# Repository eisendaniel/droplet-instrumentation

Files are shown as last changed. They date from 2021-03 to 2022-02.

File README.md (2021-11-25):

# Repository Directory Structure

### Documents

Any files which aren't _Literature_, i.e. anything that won't or can't be cited.

### Literature

A flat folder containing PDF copies of anything that will or could be cited in the reports: journal articles, tech notes, etc.  There should be a BibTeX `.bib` bibliography file at the same level as the PDF files, for use with the [JabRef](http://www.jabref.org) open source bibliography and reference manager.

### Presentations

The files used in any presentations, including the final presentation.

VBUS
* R, Matlab, etc. files, containing _only_ the figures used in the report at this level.
* One sub-folder "Figures" to keep figures organised.

Home: O
Res: 55
Targ: 172

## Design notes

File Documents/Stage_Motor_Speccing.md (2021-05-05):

# XYZ Stage Motorisation

Applying motorisation and actuation to the droplet dispensing process and support stage. Pulse Z to detach droplet, rotate around Z to position pipette etc.

## Suppliers

servocity.com -   they have a variety of servos and motors, as well as 
mechanical mounting options. note these are largely imperial 
measurements. (mil, inchs, feet etc)

gobilda.com - other side of servocity, dealing with metric units.

pololu.com - large selection of steppers motors and servos.

robotshop.com - another large selection of servos and steppers.

* All of these suppliers are based in North America, 
* 7-10 days from there (Loss of guarantee due to COVID).

## Driving Options

###  Hall Encoder Brushed N20 motors

e.g https://www.servocity.com/90-rpm-micro-gear-motor-w-encoder/
* $USD 12-20
* 90-4900RPM
* Drive a worm gear to rotate platform
* Require manual position control

### Worm Gear set
* https://www.servocity.com/27-1-worm-gear-set-1-4-bore-worm-hub-mount-worm-gear/

### Servo driving
e.g. https://www.servocity.com/hs-311-servo/
* When driving with a uC, wide signal ~200 degrees
* Pulse to position
* Nylon - wear/no backlash
* Metal - vis versa

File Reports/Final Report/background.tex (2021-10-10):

\chapter{Background and Related Work}\label{C:back}

\section{Droplet Impact \& Evaporation}
Droplet Impact and Evaporation experiments have a consistent list of instrumentation requirements and variable considerations. At its core is the substrate upon which the droplet is deposited, this can be held at a variety of temperatures, have differencing surface and material properties that all affect the temperature evolution and physical interaction between the droplet and its surface. Secondly is the method of droplet dispensing or deposition, and third is the method through the which the experiment controls for, account for, or just records the variety of affecting factors.      

\subsection{Other Approaches}
In literature, there exists a variety of rigs for similar experiments. These were explored to gauge a range of what factors were controlled (and measured) and with what approaches. In summary:
\begin{itemize}
    \item Controlled environmental factors with basic box \cite{step_book} or measured factors only \cite{measure_only}.
    \item Controlled for droplet position and volume with hard-mounted pump plus needle, but lacks environmental control or automation, and there is no top-view camera \cite{non_newt} \cite{fixed_pump}.
    \item Incorporated stepper motor driven automation, but no environmental control or monitoring \cite{motors}.
    \item Full environmental chamber and fixed droplet pump, but the single camera, has the separate uncontrolled rig for top view \cite{duel_rig}.
\end{itemize}

\section{Background on Stepper motor control}
This section will cover the background of controlling bipolar stepper motors via a step/direction style driver setup, as its concepts will be mentioned later in the report. This is a focused background on the key considerations and requirements when designing for and operating this specific subset, and by no means applicable to all driving and specific motor choices.

The stepper motors provide precise positioning and are capable of moving their rotor to a specified position and holding that position at a wide range of load torques. This capability makes the stepper motors popular in optics, medical instruments, factory automation, and industrial equipment.

The typical topology of a stepper driving system (based around the step/direction method) consists of a controller, driver, and stepper motor. The controller provides a direction  signal and step pulses, while the driver converts these signals into actual electrical power and supplies them to the motor. The stepper motor moves in steps, each step covering one step angle, which can be described as the rotor displacement corresponding to one step pulse \cite{step_app}.

Stepper motors typically have a step size specification (e.g. 1.8° or 200 steps per revolution), which applies to full steps. Step/direction drivers usually provide a 'microstepping' mode which increases the resolution by allowing intermediate step locations, which are achieved by energising the coils with intermediate current levels \cite{step_book}.

The last major consideration in driving steppers is controlling the start-up and stopping speeds for the controller's provided pulse train to the driver. As the motor is a mechanical device in the real world, expecting a perfect impulse response will lead to driving failure. Inertia ratio is critical to stepper motor acceleration \cite{step_book}. Too great a difference in inertia ratio between system and motor risks missed steps or stalling the coils. So when starting a stepper motor, acceleration and deceleration should happen through pulses to the motor that starts slowly and gradually quicken in a process called ramping.

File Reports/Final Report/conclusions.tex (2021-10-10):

\chapter{Conclusions and Future Work}\label{C:conclusion}

\section{Conclusions}

The aims of this project were to control for variations in droplet morphology; droplet position and volume, providing an improvement over the previous system. Produce an extendable platform that enabled the experimental process to be automated/centrally controlled to speed up the procedure. Provide a data collection system for uncontrolled factors. 
These goals were chosen with the hypothesis that improving the system's performance in these aspects would carry through to an improvement in the inconsistent results observed in the previous iteration of the system.  

To control for droplet volume and provide a method for variable volume, this project utilised a pre-calibrated electronic pipette as the central droplet dispensing tool that is interfaced with to provide remote GPIO control. Automation, user control and positional control was achieved via a serial command-driven stepper motor controller that drove the motion of a micrometer controlled XYZ stage mounted upon an optical breadboard.   

\subsection*{Successes}
The use of a pre-calibrated electronic pipette eliminates volume variation to a point beyond the scope of this projects ability to measure, but more importantly, the mechanical system was confirmed to be stable enough to support the full variable volume range from 0.5 to 10 microlitres.

The stepper motor driving system parameters were successfully tuned to reduced pipette tip settling oscillation below 1mm in 1s and achieves consistent and exact positioning. This precision in instrumentation control resulted in the reduction in droplet positional offset  variance from 0.296mm to 0.018mm.

From initial analysis of the collected temperature profiles, this project can preliminarily confirm the hypothesis that improved positional and volume consistency will result in greater consistency in experimental results. Though more data is needed.

The firmware and controller implemented fully supports input of predefined command sequences that allows a user to quickly run the same complex experimental procedure much time, with the exact same instrumentation performance.   

\subsection*{Drawbacks}
Major drawbacks of the resulting design include the XY positional locking of the pipette stage due to static Z motor mounting on the breadboard. This results in any required adjustment to the camera, substrate and reservoir to be carried out to fit the pipette stage position.

This implementation lacks auto-homing to set zero position, and additionally due to the permanent magnetic pole of the stepper motor stator combined with the drivers micro steppers, the user can request an invalid holding position as home. This cannot be maintained due to current limits and will snap away from it. This should however be evident in the setup stage of the experiment.  

\section{Future Work}
As stated this project produced an extendable platform from which a variety of features can be implemented.
\begin{itemize}
    \item User-Friendly Graphical Control to interface with serial command controller. As of now, there exists a LabVIEW script that can interface with the serial input of the controller but more in-depth user-friendly version would be a great step up in the usability of the system.
    \item Due to the projects nature combined with an inopportune COVID19 lockdown the integration of homing switches to automate setup was planned but not implemented. This addition would increase setup speed and usability.
    \item Utilise included GPIO breakout header to synchronise external data acquisition
    \item Further investigate Temperature evolution with varied volume, substrates, cleaning techniques
    \item Add enclosure to isolate air currents and further control variables.
\end{itemize}

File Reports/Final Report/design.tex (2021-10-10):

\chapter{Design}\label{C:des}

\section{Project Specifications and Justifications}
Given the results of the initial evaluation, the project can now be constrained. Its main goals are to eliminate volume variation, control for droplet position, enable automation to reduced time between consecutive runs. It will not control, but provide data-logging for the environmental effectors; temperature, humidity, pressure.

From this there is a number of requirements to consider:

\begin{itemize}
    \item \textbf{Mechanical Stability}
    \item \textbf{Droplet Position Repeatability}
    \item \textbf{Consistent and Variable Volume}
    \item \textbf{Process Automation}
    \item \textbf{System Expandability}
\end{itemize}

The project will be evaluated on how it meets the above Specifications, its ability to control for volume and positional accuracy and repeatability as well as how it adds/improves automation, provides environmental data and allows an extension.

\section{Drop Dispensing and Volume Control}

At the core of the system is the liquid droplet dispensing hardware. The two core limitations of the initial setups manual syringe were fixed volume dispensing and the observed inconsistency in drop volume. In order to address these, an alternative solution is required to provide a core that allows the rest of the project to control and automate positioning, dispensing and liquid refilling. It was decided early on that the bulk of custom design would be focused on the motorisation hardware, custom mounting, and the driving software so the dispenser would be handled by a pre-existing product. The product selected for this is a single channel electronic pipette from Labnet, P3600L-10. 

\begin{figure}[h]
    \centering
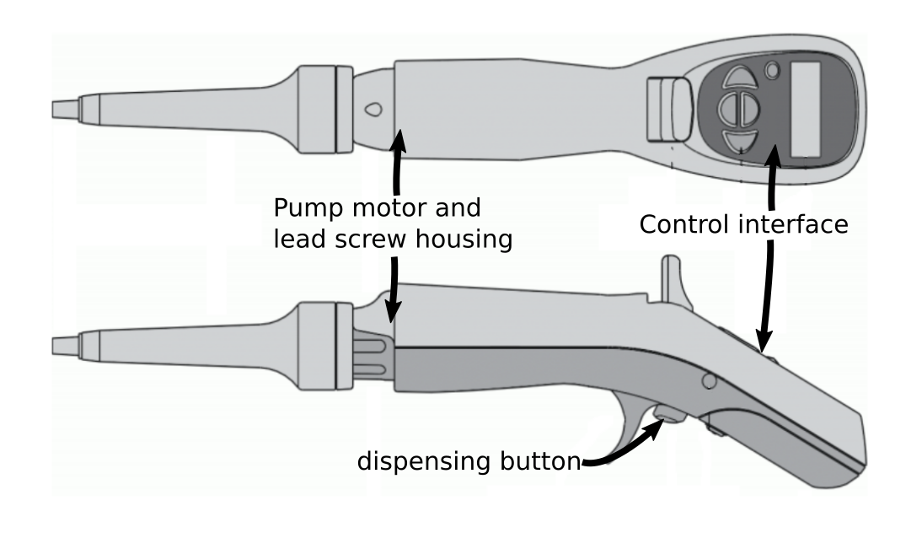
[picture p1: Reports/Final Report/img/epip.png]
    
    \caption{Labnet Excel P3600L-10}
    \label{fig:pip_dia}
\end{figure}

This product comes recalibrated and verified to dispense a droplet at a specified volume with an accuracy of $\pm 4.0\rightarrow \pm 1.0 \%/\mu L$ over the selection range of $0.5\mu L \; to \; 10\mu L$. This range represents the full range the pipette itself is capable of drawing and dispensing, configured via the front panel [see \ref{fig:pip_dia}], but an evaluation of the integrated system is required to confirm the mechanical stability is high enough to prevent a high volume drop from prematurely detaching, as well as if its capable of depositing the minimum volume on the substrate.

Liquid refilling and dispensing are handled via the button on the back [\ref{fig:pip_dia}] and to enable the instrumentation to centrally control this, the planned approach was to break out the underlying switch contacts as GPIO inputs. The full process and results will be fully explored in this reports implementation system.

\section{Mechanical Design}

The goals for the mechanical aspects of this project are to provide a mounting interface to allow for the movement and positioning of the electronic pipette, mount to the optical XYZ stages, and transfer the driving force from the stepper motors to the instrumentations mechanisms.

All mechanisms share the requirements to fit compactly and correctly on the optical breadboard baseplate. Be designed in such a way as to minimise backlash and prevent vibrations from propagating and resonating through the system. As this could interfere with droplet dispensing; increasing pipette tip overshoot and settling times, causes prematurely drop detachment and generally decreasing the key performance metrics.

\subsection{Rotating Pipette Mount}

The first half of the main assembly is Pipette Stage. In order to manoeuvre the pipette from the reservoir to substrate stack, the pipette needs to be held at a specific height and angle to roughly match the central stage (as it is Z adjustable) and rotate between these two points.

To achieve the mounting stage consists of three main parts: 
\begin{itemize}
    \item Pipette clamping and Angled mount: Responsible for securely fastening the e-pipette at the correct angle.
    \item Laser Cut Mounting Tower: Sets pipette height and connects pipette to the motor.
    \item Motor shaft interface and Stage Fastening: Rotation is directly driven via the motor, thus the assembly is mounted to the motor shaft. 
\end{itemize}

Dimensional Specifications: Pipette height of 130mm (from breadboard) and angle of 36.25 degrees.
These specifications are used to derive the full dimensions of the following assemblies.

The electronic pipette form-factor is ergonomic-hand to fit in human hand-so the clamping mechanism to fit it to the tower plate itself was challenging to design to successfully restrict its rotation and backlash. 3D printed PLA c-clamps were the perused approach to capitalise on the materials ability to deform and to aid in rapid implementation and testing.

\begin{figure}[h]
    \centering
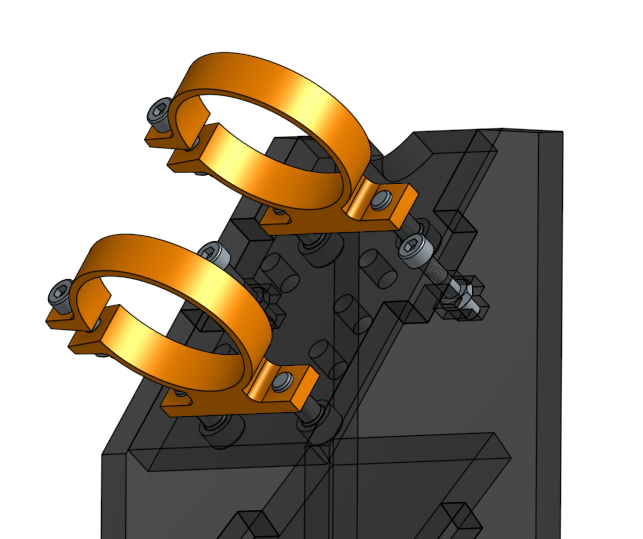
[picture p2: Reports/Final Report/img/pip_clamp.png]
    
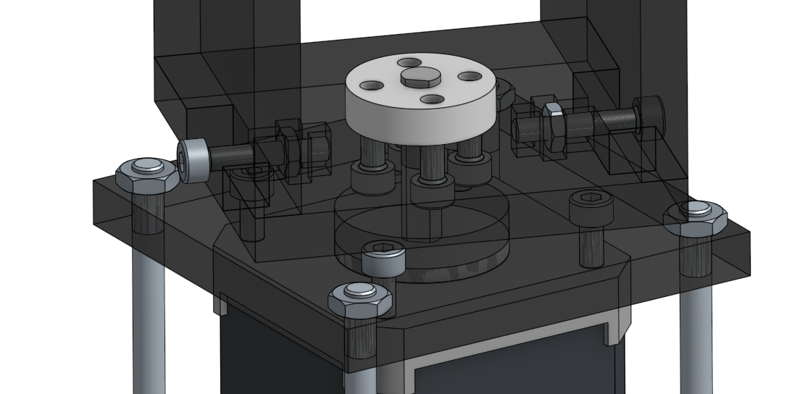
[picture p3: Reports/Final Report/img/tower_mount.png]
    
    \caption{Left: Pipette Clamps and Tower, Right: Towers base mounting to the motor shaft}
    \label{fig:tower}
\end{figure}

The base design used to accomplish this was a 3D-printed ring clamp [Left:\ref{fig:tower}] meant to be tightened and fit to the unique form of the pipette body. A variety of ring sizes and gap distances were printed and test fitted. From this, it was determined that a ring diameter of 32mm and a gap of 6mm fits and deforms to the shape of the pipette. However, there was still some rotation and slip so a notch was cut into the acrylic angle plate [Left:\ref{fig:tower}] to slot the pipettes support rest and a second ring clamp (36mm) attached lower down of the body.

To connect the tower assembly to the motor and optical stage\dots

\subsection{Z micrometer Control}

In order to control the height of the pipette tip; to enable automated refilling and to place the dispensed droplet onto the substrate the Z height of the optical stage needs to be motorised. The Z height has a manual control in the form of an adjustment micrometer that allows for 10mm of travel, but this presents the first problem in design.
The micrometer travels linearly throughout the adjustment, i.e. if the stage raises 10mm the knob will retract 10mm also. Due to this a custom shaft coupler is required to interface a fixed motor to the moving knob.

\begin{figure}[h]
    \centering
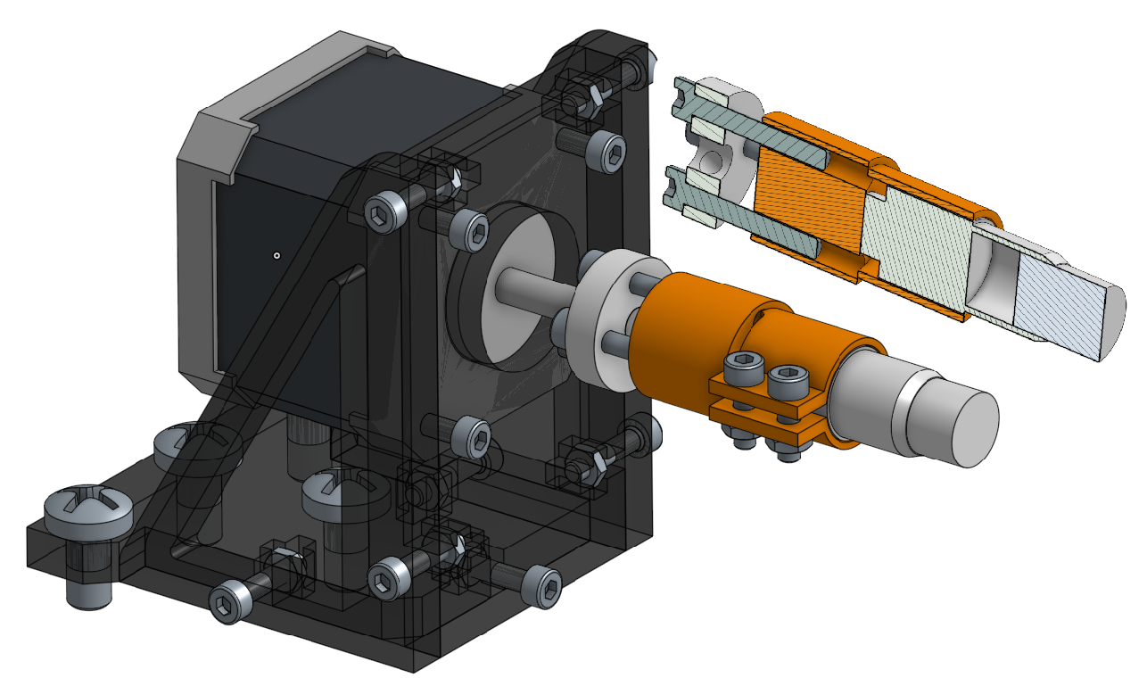
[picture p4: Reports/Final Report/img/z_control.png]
    
    \caption{Z Driving Motor and Sliding Shaft Coupler}
    \label{fig:z_coup}
\end{figure}

The figure above[\ref{fig:z_coup}] shows the assembled design. One end of the coupler is an extended c-clamp that mates with the knurls knobs of the micrometer and the other is a solid piece with 4 M3 clearance holes. These holes interface with a universal shaft-hub mount with 4 M3 machine screws that transfer the rotation of the motor and allow the coupler and knob to slide away over the course of a movement.

The key limitation of this design is that is constrains the XY position of the stage to a single setting. This is due to the motor being fastened to the breadboard baseplate more stability, alignment and vibration reduction. Because of this it moves the fine positioning to the other stages in the setup; substrate stack and cameras. 

\section{Electronic Design}

\subsection{Motors}
The motion required for the motors in this system is to provide rotation about the vertical axis to the mounted pipette, to swing from above the substrate to out of the camera view and over a refill reservoir, as well as continuous rotation to interface the Z axis control for droplet depositing and possible refilling.

Stepper motors allow for both precise position control without the need for a feedback system and are capable of continuous rotation. In comparison, brushed/brushless DC motors require encoders for positional control and servos may do either but not both continuous rotation and positioning.

NEMA17 standard-sized steppers were chosen to best fit the dimensions of the XYZ optical stage (60mm plate to 40mm motor frame) with room for fastening hardware. That left two choices for the top R stage motor; full size 38mm high frame or shorter pancake frame. Even though the pancake frame would reduce the overall height of the system, the shaft length available for this motor is less only 7mm and would greatly restrict the mounting options of the tower to the motor. For this reason, 2 NEMA17x38mm Stepper motors were chosen.

\subsection{Motor Driving}

\subsubsection*{The Requirements}
To drive the selected stepper motors, discrete step/direction style micro stepping drivers were chosen. This allows for the design to be flexible with its electronics placed to accommodate the experimental needs. Allows for a fairly agnostic choice for the controller to supply the control signals, and standardised pinouts allow for requirement flexibility and replacements.

\begin{table}[h]
    \centering
    \begin{tabular}{|l|l|l|l|l|}
        \hline
        \textbf{}     & \textbf{A4988} & \textbf{DRV8825} & \textbf{STPIN820} & \textbf{DRV8834} \\ \hline
        Step Res      & 1/16           & 1/32             & 1/256             & 1/32             \\ \hline
        Logic Level   & 3V3/5V         & 3V3/5V           & 3V3/5V            & 3V3/5V           \\ \hline
        Current Limit & 1A             & 1.5A             & 0.9A              & 1.5A             \\ \hline
        Drive Voltage & 8-35V          & 8.2-45V          & 7-48V             & 2.5-10.8         \\ \hline
    \end{tabular}
    \caption{Comparison of considered drivers}
\end{table}

Main consideration for device choice are: micro step resolution, driving current limit (passively cooled), and configuration pinout.

\subsubsection*{The Choice}
The DRV8825 was ultimately chosen.
\begin{itemize}
    \item High microstepping resolution, lower than the STPIN820 but cheap high-resolution driver is prone to step skipping \cite{step_book}
    \item Highest driving current as torque requirements are unknown for this design the headroom is nice even if it isn't used, especially as it will run cooler at lower power draw.
    \item It ranked above the DRV8834 due to it configuration pins (to set microstepping mode) as it provides all 3 pins without the requirement to leave pins floating as a setting thus allowing for full software control.
\end{itemize}

\newpage
\subsection{Environmental Monitoring}

Although the aim of this project is to only control the position and volume of the droplet in the experiment, to at least fully address the list of affecters [covered in \ref{C:init_eval}] the environmental factors recorded are: \textbf{Temperature, Barometric Pressure, Relative Humidity}.

As this section of the project doesn't note share resources with the main motorised assembly it key design considerations was simplicity and function.
Therefore, the environmental monitor is not required to have any integration with the main controller or data logging capabilities.

To meets these requirements the monitor was decided to be a low power microcontroller + OLED display stack that polled environmental sensor peripherals. This would be battery powered and utilised low power sleep modes to extend lifetimes.

To facilitate ease of implementation the microcontroller + display combo was chosen to be an Adafruit feather and OLED stack. specifically the RP2040 for its low power capabilities and JST LiPO battery connector.

Sensor options considered were the discrete LPS22/25 for pressure and DHT11/22 for humidity and temperature or the fully integrated BME280 for all measurements. 

\section{System Overview}

\begin{figure}[h]
    \centering
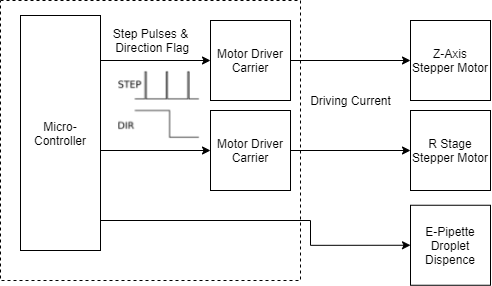
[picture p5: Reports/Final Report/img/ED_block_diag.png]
    
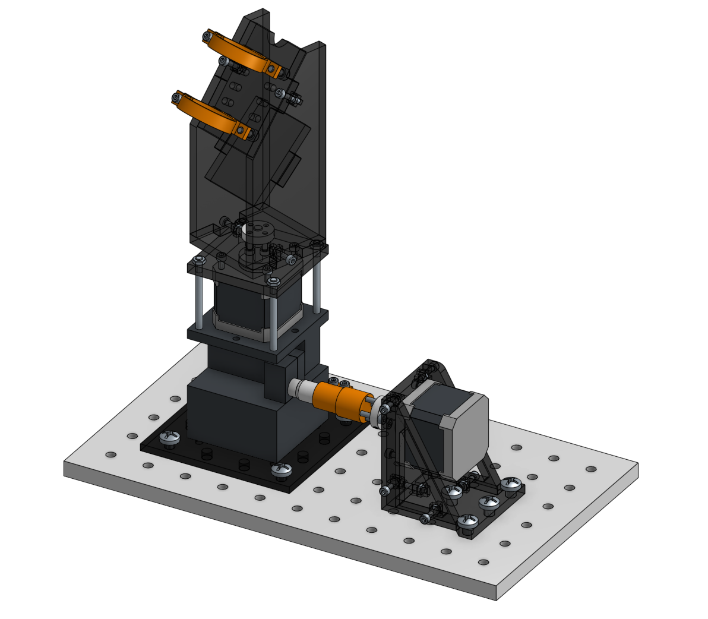
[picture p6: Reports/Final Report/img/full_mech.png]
    
    \caption{Left: Instrumentation Architecture, Right: Full CAD Design and Layout on optical breadboard}
    \label{fig:sys_des}
\end{figure}

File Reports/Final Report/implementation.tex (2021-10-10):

\chapter{Implementation}\label{C:imp}
The implementation process took the planned designs and selected hardware and constructing an integrated system. This provided an opportunity to test, iterate finalise the designs and approaches of the project.      

\section{Mechanical Components}
Implementing the mechanical components of the system covered the material choice, manufacture and adjustment of the motor mounting brackets, shaft couplers and interfacing and pipette mounting and supports. Considerations taken were speed of iterations. Flexibility in adapting specific dimensions to suit needs and to maximise reliability and stability. 

\subsection{Rotating Pipette Mount}
The C-clamp's design did not fundamentally change from the initial design, and remained the duel clamping system with matched internal circumferences. They did however go through many smaller interactions to achieve the preferred performance. Firstly, obtaining the required internal circumference of the clamps from the asymmetric body of the pipette was taken using a length of string was used to at the points of intended fastening. The clamping pressure then deformed the initially circular parts to the ergonomic form of the pipette body.

\begin{wrapfigure}{r}{0.3\textwidth}
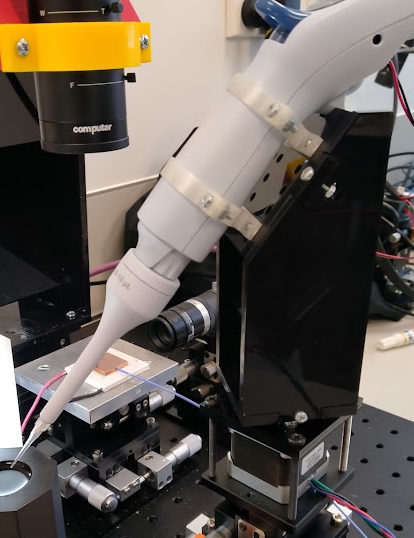
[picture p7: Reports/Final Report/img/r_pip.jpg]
    
    \caption{Final constructed Pipette stage mounting tower w/ clamps and motor}
\end{wrapfigure}

This process, and the resulting measurements of 32mm and 36mm remained unchanged.
However, the ring thickness was varied and tested. 3 options were 3D printed and trialled; 1mm, 1.5mm, and 2mm. This thickness affected the clamps ability to deform to the shape of the pipette, how rigid the mounting was and the strength at the clamping screw holes.

1mm was used for the longest initially, but had a noticeable woggle as well and resulting in the screw hole delaminating from the ring due to flexing in the plastic. After this failure, the 1.5 and 2mm versions were printed and trialled for a shorter period. The 2mm provided much better strength, showing no noticeable degradation at points of high-stress concentration. However where this thickness failed was in deforming, the added rigidity was just too inflexible to ever fully clamp and resulted in play/slippage. Given this, two 1.5mm version were printed to compromise and successfully deformed and remained intact over the remaining project time.   

Another area of tweaking was the screw tolerance. These pieces were designed to take advantage of the plastics deformation to also allow for the screws to cut their own threads as provide a stronger grip. As the screw is initially inserted a too smaller hole can result in splitting delamination of the plastic layers, via experimentation, a +0.2mm diameter tolerance allowed for retaining that 'self-tapping' characteristic while maintaining structural integrity. 

The tower itself was designed to be fully laser cut from acrylic to minimise [material] flexibility and to aid to modularity. This allowed the height to be adjustable by cutting different side pieces for example. This did not deviate from design, but initially, the tower was glued together to reduce weight but this was quickly scrapped for machine screw bolting, with the intention that any oscillations or resonance in the system would be tuned for on the motor driving side of the project.

\subsection{Z micrometer Control}

The Z height adjustment represents the most sensitive mechanical system and required careful measurements to axially align the micrometer knob and the shaft as well as matching the coupler length to accommodate the discrete fastening points of the optical breadboard. 

\begin{wrapfigure}{r}{0.42\textwidth}
    \centering
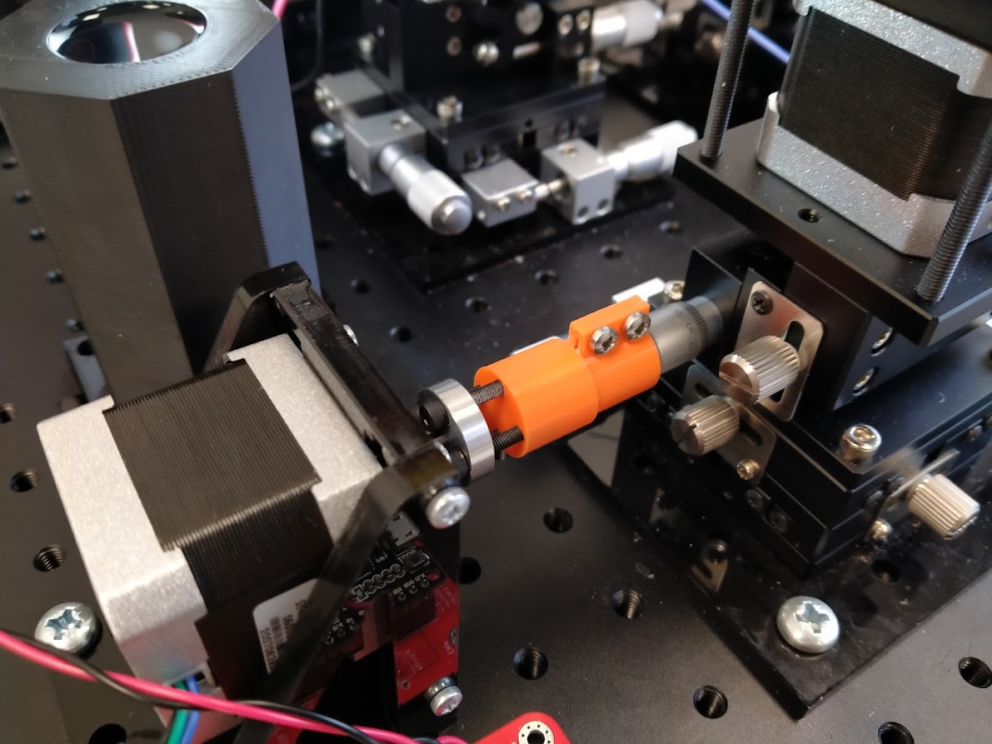
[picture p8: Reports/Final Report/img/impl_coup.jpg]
    
    \caption{Constructed Motor mount and sliding coupler interfacing with the z-micrometer of the XYZ stage}
    \label{fig:z_coup}
\end{wrapfigure}

The figure above \ref{fig:z_coup}shows the Z-motor statically mounted to the breadboard with a laser-cut bracket assembly. This, along with the aforementioned tight tolerance requires presented the first problem to overcome with mechanical performance.

The initial z-coupler was printed with a 1mm defect in it radius as too small M3 screw holes. This cause splitting under high load as well as large vibrations that propagated through the whole system as was causing premature droplet detachment.

After reprinting the coupler, these vibrations were greatly reduced by still present. To combat this, the motor driving parameters were adjusted, slowing the signal speed from 10 revolutions per second until it no longer resonated during the adjustment. Final parameters were 6 rev/s and 100 rev/s/s.

\section{Electronic Components}

The aim of the electronics in this project is to provide an interface for the host computer to send commands with the controlling microcontroller and supply and support the stepper driving stages and their required current. The microcontroller receives command strings over serial USB and parsed them and executes them either at PWM control signals to the STEP inputs of the drivers or digital flag signals to the pipette. The driver requires a motor supply voltage of 8.2 – 45 V. This supply should have appropriate decoupling capacitors close to the board, and it should be capable of delivering the expected stepper motor current.

These decoupling capacitors are to act as reservoirs for high loads and shield the onboard low-ESR ceramics from LC voltage spikes. These spikes can exceed the 45 V maximum voltage rating for the DRV8825 and permanently damage the board, even when the motor supply voltage is as low as 12 V. This was addressed with the addition of  a pair of 100u electrolytic capacitors across the motor power rails right next to the carriers.

\begin{figure}[h]
    \centering
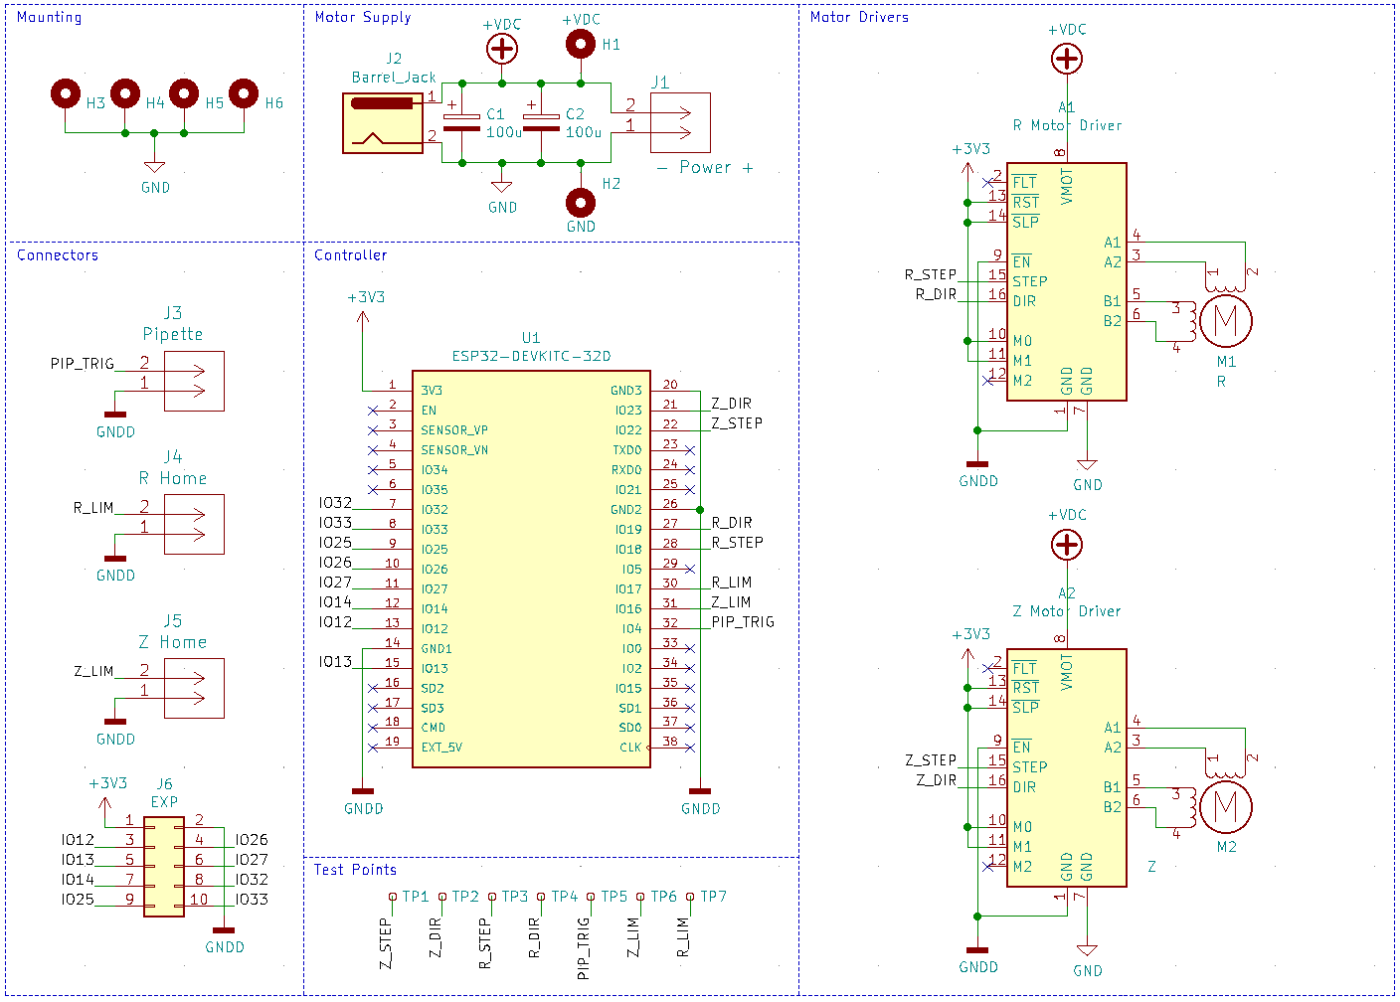
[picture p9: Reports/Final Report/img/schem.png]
    
    
    \caption{Left: Controller Schematic and Right: Constructed PCB}
    \label{fig:schem_pcb}
\end{figure}

The figure\ref{fig:schem_pcb} shows the final electrical implementation and state the controller PCB (only partially populated due to COVID shipping delays). Note that this design included unfulfilled homing switch pads, as well as a 10 pin GPIO breakout for future expansion; i.e. external data acquisition syncing or other communication options.

The final consideration for this construction is whether the driver carriers require heatsinking or cooling. The DRV8825 driver IC has a maximum current rating of 2.5 A per coil, but the current sense resistors further limit the maximum current to 2.2 A, and the actual current you can deliver depends on how well you can keep the IC cool. The carrier’s printed circuit board is designed to draw heat out of the IC, but to supply more than approximately 1.5 A per coil, a heat sink or other cooling method is required. To obtain the systems requirements, both motors were supplied with a 15V DC motor voltage and the total current draw was tested at holding and under load.

This resulted in a max single driver holding current of 0.41A and a peak load current of 0.58A. 
This is well below the uncooled limit so no cooling solution was supplied.

\subsection{Motor Driving}
\subsection{Setup and Requirements}
To meet the driving requirements of the stepper motors outlined in this reports background [\ref{C:back}], preventing stalling and minimising harsh start stop behaviour that could cause unwanted vibrations, the controller and driver must be verified to be able to supply the step pulse train with ramping speeds and characterise the motors to ensure no steps are skipped. If this occurs the open loops control scheme will mean that the systems positional accuracy will fail.  

Test driving firmware was implemented on an ESP32 to validate its ability in producing the required pulse train step signal. The controller was required to produce N steps (pulses) at a set average speed, and ramp-up and down that pulse speed at the head and tail of that signal.

Set values of 200 steps forward and back, at a speed of 200 steps per second, with max acceleration of 800 steps per second per second:

These pulses were captured on a second microcontroller listening for falling edges to trigger an interrupt routine to record and display that data.

\subsection{Results}

\begin{figure}[h]
    \centering
    \begin{subfigure}{.45\textwidth}
        \centering
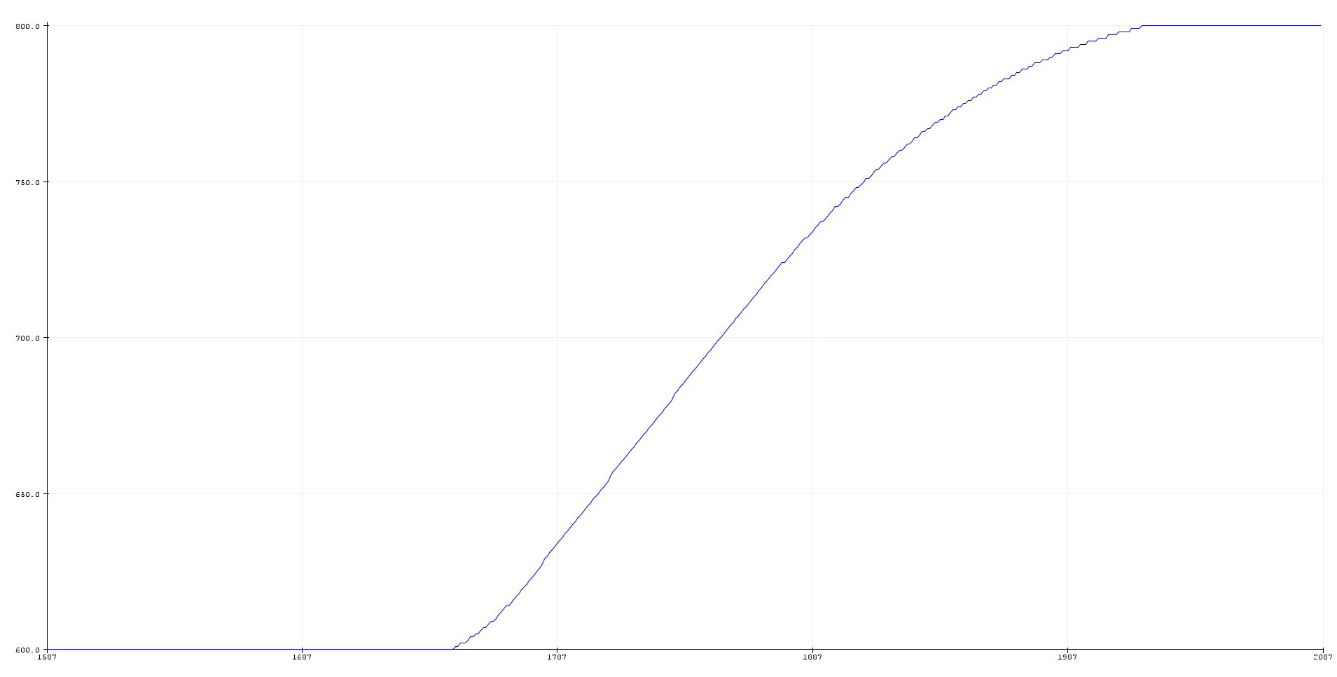
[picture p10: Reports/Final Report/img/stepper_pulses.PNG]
        
        \caption{Pulse Count}
    \end{subfigure}%
    \begin{subfigure}{.45\textwidth}
        \centering
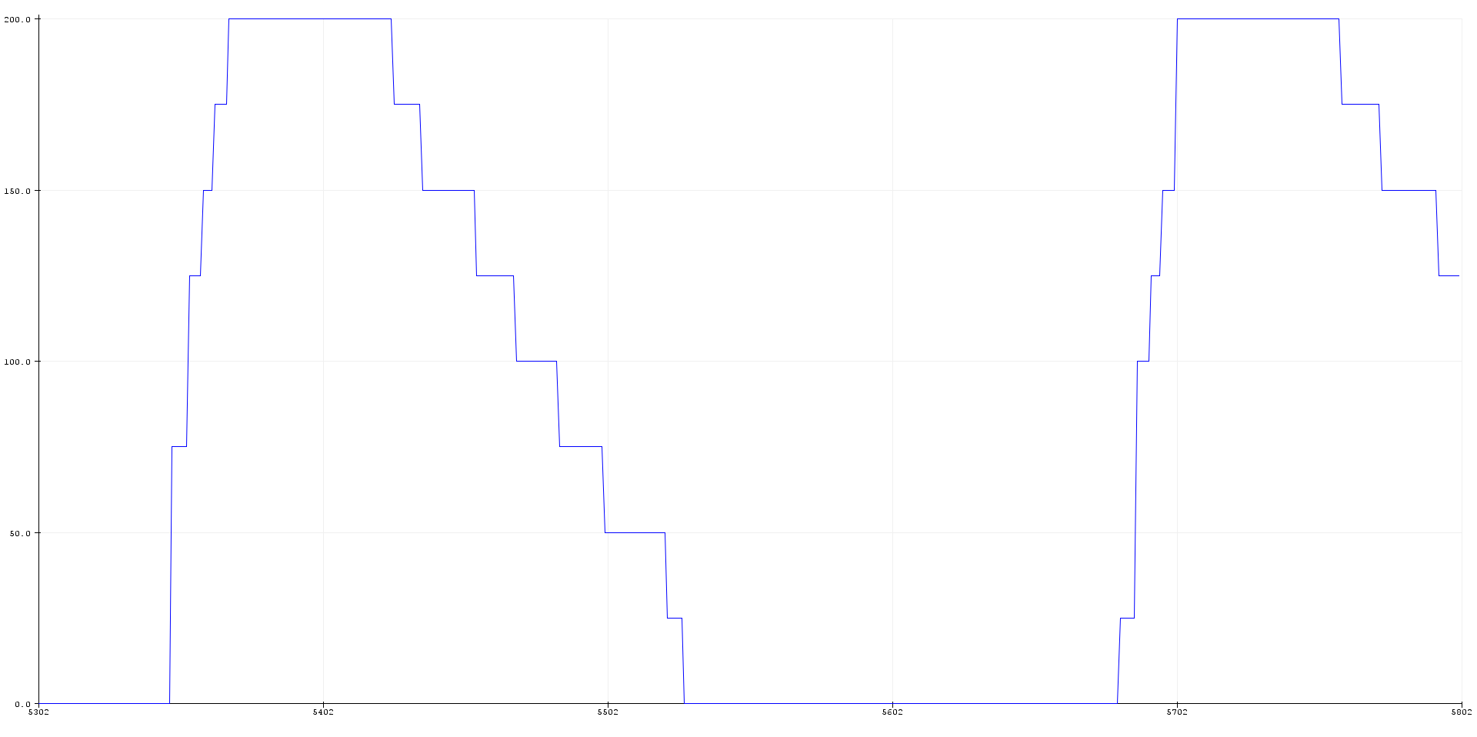
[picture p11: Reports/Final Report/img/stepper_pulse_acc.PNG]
        
        \caption{Pulses per Second}
    \end{subfigure}
    \caption{}
    \label{fig:code}
\end{figure}

Figure \ref{fig:code}:a shows a successfully produced signal of 200 pulses with an inferred acceleration at its head/tail. This speed ramping is better illustrated in figure \ref{fig:code}:b showing the stepping change in pulses per second over the course of the pulse train.

Additionally, it was found that these motors experiences some resonance and began skipping step when in 1:1 driving mode at the specific frequencies of 90Hz, 100Hz and 180Hz. This was solved by enabling the driver carrier's 1:32 microstepping mode and modifying the firmware to match.

\subsection{Pipette Triggering}

The pipette draws and dispenses liquid be using an internal DC motor to drive a leadscrew pressure chamber. This is controlled via a multi-function switch on the DC input daughter board. This daughterboard was required to be removed to gauge the signal requirement needed to trigger this event. 

\begin{figure}[h]
    \centering
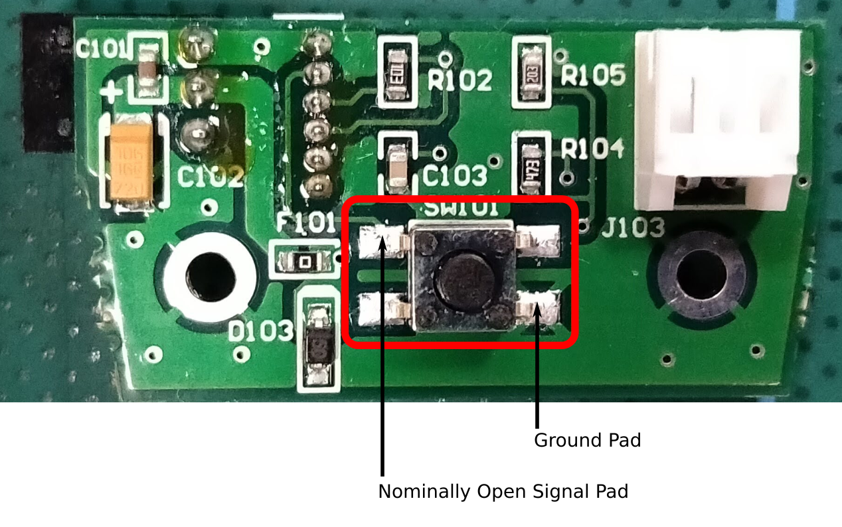
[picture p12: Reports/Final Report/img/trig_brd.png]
    
    \caption{E-Pipette dispensing trigger switch daughter board with exposed pads}
\end{figure}

From this investigation, it was determined the internal GPIO was connected to the nominally open (unconnected) pin of the switch. When actuated this line is pulled down to ground indicating a button press. This triggers 1 of 2 actions; Pipette wake-up or toggle leadscrew position, either dispensing or refilling the reservoir tip.   

To automate this process the nominally open pad was broken out to an output GPIO line on the controller and the ground was broken out and shared with the signal ground of the controller.

\section{Software}

\subsection{Instrumentation Controller}
ESP32 based system controller with serial interface for issuing commands. Provides functionality to:
\begin{itemize}
    \item Motorised stages, height and angular position
    \item e-Pipette droplet dispensing
\end{itemize}

The architectural approach for this controller is to provide an extendable and versatile command interface that allows for multiple input/control methods. For this reason, a continuous serial string input is polled for, parsed into internal library calls that control the motor driving signals and pipette actions. This allows the controller to be interfaced either directly with a text input serial command line, a LabView VISA serial control script or via a custom host side script.

\begin{figure*}[h]
    \centering
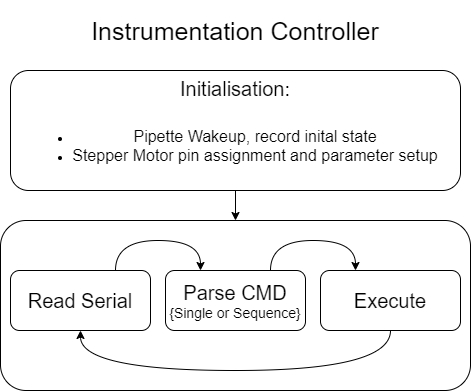
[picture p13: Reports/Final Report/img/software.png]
    
\end{figure*}

Upon boot, the firmware pings the pipette to wake it from sleep. Sets up symbolic motor objects to control signal generation with the correct micro steps, speed and acceleration terms. Then enters a command poll, parse and execute loop.

This command loop, translates real-world input units and translates them to the required step count.
For example to rotate the pipette by half a revolution the command \texttt{R 0.5} is sent, and to raise the pipette by 5mm, \texttt{Z 5mm}. The full command list is as follows: 

\begin{table}[]
    \begin{tabular}{|l|l|}
    \hline
    \texttt{ADJ R or Z {[}n\_steps{]}} & Debug command to allow individual stepping of motor \\ \hline
    \texttt{R {[}n\_revs{]} }       & Primary Pipette rotation, in revolutions            \\ \hline
    \texttt{Z {[}n\_mm{]}          }& Primary Z height adjustment, in mm                  \\ \hline
    \texttt{DEL {[}delay\_time{]}  }& Add time delay in ms                                \\ \hline
    \texttt{PIP {[}UP|DOWN{]}      }& Draw liquid (UP) or dispense (DOWN)                 \\ \hline
    \end{tabular}
    \end{table}
    
Internally the firmware keeps track of the last pipette action to ensure the user does not accidentally dispense or draw liquid.

To enable setup and tuning as well as full experiment automation there are two command input modes. Individual and Sequence. To enter a sequence, the special command \texttt{SEQ} is sent follows be semicolon-separated commands, \texttt{Z -5; PIP UP; Z 5; R 0.25; DEL 200; PIP DOWN; Z -4; Z 4; R -0.25; END;}.

This firmware produces two main parameters that are available for tuning when evaluating the performance of the integrated system: The step signals pulse speed, and its ramping acceleration.

\section{Environmental Monitoring}

\begin{figure}[h]
    \centering
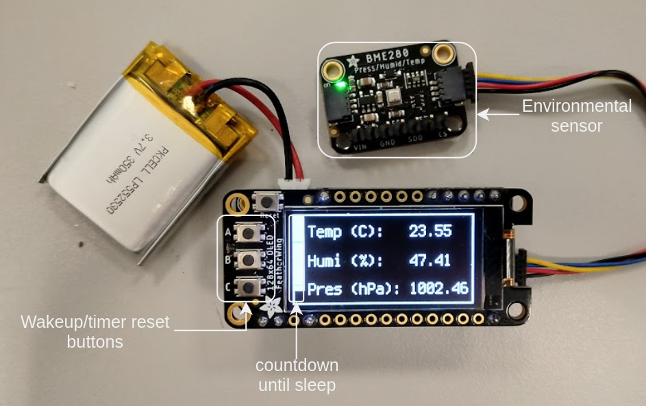
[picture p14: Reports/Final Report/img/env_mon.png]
    
    \caption{Implemented Environmental Monitor}
\end{figure}

The design values speed and quick integration, so assembly was plugin-play. The primary work down was the power management and data-collection software. The BME280 and OLED screen are attached to the I2C bus with unique addresses. These are polled to retrieve prefiltered temperature, pressure and humidity data and pushed to the screen.

\subsection*{Low Power}
As the system is portable and powered only by a single cell LiPO battery, long life is more of a requirement than continuous display, as the data is only needed to be noted at the beginning of an experiment. To achieve the firmware attaches button alarm interrupts to OLED screens buttons and counts downs an internal timer. Upon timeout this firmware clears the OLED, places the screen and BME in sleep mode. These will now draw $5\mu A$ and $2 \mu A$ respectively. The RP2040 itself then enters deep sleep, clearing memory and shutting down most of its hardware, achieving $180\mu A$ of draw. 

\section{Full System}

\begin{figure}[h]
    \centering
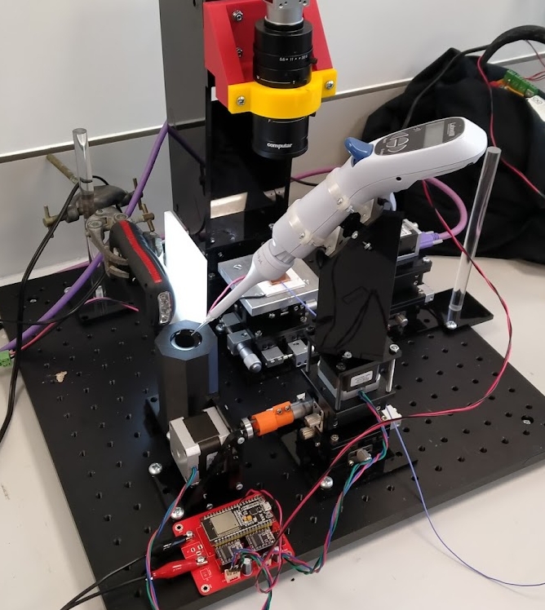
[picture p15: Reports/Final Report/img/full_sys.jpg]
    
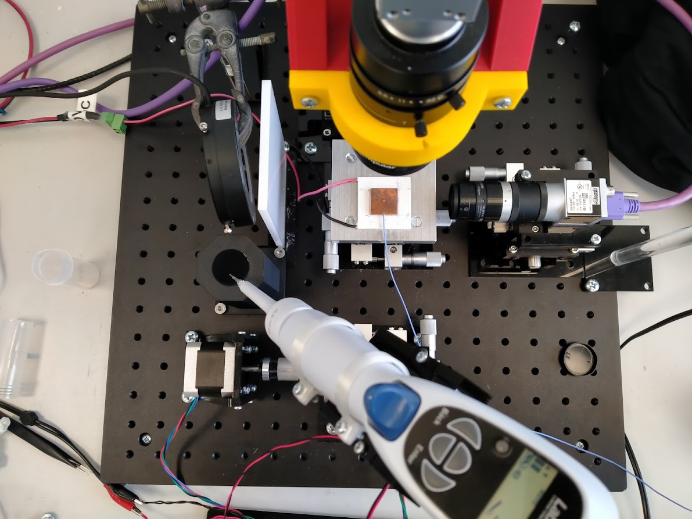
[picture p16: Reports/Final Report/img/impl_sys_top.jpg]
    
    \caption{Full System}
\end{figure}

Fully integrated, this system is assembled on an optical breadboard with an assortment of adjustable XYZ micrometer stages; camera mounts, backlight and diffusers, a liquid reservoir and a central substrate stack. The procedure this instrumentation follows is: lower pipette tip into the static reservoir and draw pre-programmed volume into tip, raise pipette to the required height, rotate to depositing point, dispense droplet and pause, lower and raise pipette to deposit drop on substrate, rotate pipette clear of camera view.

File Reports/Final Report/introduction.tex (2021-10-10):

\chapter{Introduction}\label{C:intro}

\section{Motivation}
The investigation of droplet impact and evaporation is an area of interest and application to various industries. Examples of these include milk powder spray drying, inkjet printing, and applications of evaporative cooling. This project will continue on from a previous instrumentation setup, evaluating its shortcomings, and designing the next generation. This is done with the intention to improve the reliability and usability of the collected data from the previous setup by better controlling for identified affecters, and introduce methods of automating the process.

\section{Proposed Approach}
This project proposes to build the next generation of this droplet instrumentation system, based on automation and motorisation with the express aim to improve repeatability, usability and reliability by controlling for variables that affects droplet position and morphology. More precisely the new system will use stepper motors and a serial control interface to automate the positioning of a droplet dispensing electronic pipette and electronically interface with it to enable remote droplet dispensing.     

\section{Goals}
The goals of the experiment are to characterise the behaviour of a droplet impacting and evaporating from a given substrate. This forms the backbone for the goals of this project:
\begin{itemize}
    \item Increased Repeatability and Reliability droplet position, volume and morphology with the intent that controlling these variables results in more consistent results. 
    \item Increase speed and usability of the experimental process via automation to enable more data to be collected more easily and consistently. 
    \item Produce an expandable platform that can be built upon beyond the scope of this project.
\end{itemize}

\section{Evaluation}
Evaluation of the success of this project is split in two:

Firstly, individual system components will be unit tested against their specifications and through the lens of improving system repeatability. I.e. Has the mechanical been designed to minimise vibration and resonance.

Secondly, as this project exists within the greater context of an existing experimental process, data from the initial system is used to form a baseline for a comparative evaluation of the project integrated system.

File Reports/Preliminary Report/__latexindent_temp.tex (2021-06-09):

\chapter{Background}\label{C:back}

\section{Current Experimental Setup}
The instrumentation as exists is assembled with an optical breadboard and XYZ(R) stages with micrometre controls. A central stage holds the substrate with internally mounted thermocouple. 2 manual focus cameras are positioned in profile and top down, and the droplet is dispensed manually via a syringe mounted horizontally to a XYZ+R stage.
The current procedure is a manual process. The syringe tip is rotated above a marked point on the substrate, and hand empties and refilled. This results in volume and positional variation run to run. These manual procedural variance is the focus of this project.

\begin{table}[h]
    \centering
    \begin{tabular}{|l|l|l|}
    \hline
                   & \textit{distance}          & \textit{measure temperate drop} \\ \hline
    Min Pos Offset & 0.71mm                     &           -1.790142
    \\ \hline
    Max Pos Offset &                            &                                 \\ \hline
                   & \textit{Volume}            & \textit{Contact Angle}          \\ \hline
    Shape Varience & $0.629mm^3$ & 25.894 degrees *                \\ \hline
    \end{tabular}
    \caption{Variance in Setup}
    \subcaption*{* note: This excluded an outlier of a almost sphereical droplet with contact angles exceeding 95 degrees}
    \end{table}

Date taken from a series of 5 droplet runs was analyses to extract the

\section{Existing Solutions}
Brief discussion of other similar experiments and rig and what problems they solve with what methods

\newpage
\section{Background on Stepper motor control}
This section will cover the background of controlling bipolar stepper motors via a step/direction style driver setup as its concepts will be mentioned later in the report. This is a focused background on the key considerations and requirements when designing for and operating this specific subset and by no mean applicable to all driving and specific motor choices.

The stepper motors are provide precise positioning and are capable of moving their rotor to a specified position and holding that position irrespective of the load torque. This capability makes the stepper motors to be used in optics, medical instruments, factory automation, and industrial equipment. The typical topology of a stepper driving system (based around the step/direction method) consists of a controller, driver, and stepper motor. The controller provides a direction signal and step pulses and direction signal, while the driver converts these signals into actual electrical power and supplies them to the motor. The stepper motor moves in steps, each step covering one step angle, which can be described as the rotor displacement corresponding to one step pulse \cite{step_app}.

Stepper motors typically have a step size specification (e.g. 1.8° or 200 steps per revolution), which applies to full steps. Step/Direction driver usually provide a 'microstepping' mode increases this resolutions by allowing intermediate step locations, which are achieved by energizing the coils with intermediate current levels \cite{step_book}.

The last major consideration in driving steppers is controlling the start-up and stopping speeds for the controllers provided pulse train to the driver. As the motor is a mechanical device in the real world, expecting a perfect impulse response will lead to driving failure. Inertia ratio is critical to stepper motor acceleration \cite{step_book}. Too great a difference in inertia ratio between system and motor risks missed steps or stalling the coils. So when starting a stepper motor, acceleration and deceleration should happen through pulses to the motor that start slowly and gradually quicken in a process called ramping.

\section{Revised Approach}
What's the plan to solve what problems with what methods:

Focus on system automating the experimental process (motorised droplet position, dispensing and refilling), minimising variables that affect the repeatability of the experiment: Ie drop volume (pipette), drop position relative to substrate centre (programmed motor).

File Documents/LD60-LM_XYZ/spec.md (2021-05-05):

# XYZ LD60-LM

1. Material: Aluminium

2. The table size: 60*60mm

3. Rail Type: V-rail (Cross Roller Guide)

4. Travel: XY: ±6.5mm, Z Axis: 10mm

5. Load: 29.4N (3kgf)

6. Accuracy: 0.01mm

7. Straightness: 0.01mm

8.  Weight: 0.75kg

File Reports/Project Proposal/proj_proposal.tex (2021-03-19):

% % $RCSfile: proj_proposal.tex,v $
% % $Revision: 1.3 $
% % $Date: 2016/06/10 03:44:08 $
% % $Author: kevin $

\documentclass[11pt, a4paper, twoside, openright]{report}

\usepackage{float} % lets you have non-floating floats
\usepackage{url} % for typesetting urls
\usepackage{graphicx}
\usepackage{subcaption}
\usepackage{hyperref}

\renewcommand{\thesection}{\arabic{section}}

%  We don't want figures to float so we define
%
\newfloat{fig}{thp}{lof}[chapter]
\floatname{fig}{Figure}

% % These are standard LaTeX definitions for the document
% %
\title{Instrumentation System for Liquid Drop Impact and Evaporation}
\author{Daniel Eisen}

% % This file can be used for creating a wide range of reports
% %  across various Schools
% %
% % Set up some things, mostly for the front page, for your specific document
%
% Current options are:
% [ecs|msor|sms]          Which school you are in.
%                         (msor option retained for reproducing old data)
% [bschonscomp|mcompsci]  Which degree you are doing
%                          You can also specify any other degree by name
%                          (see below)
% [font|image]            Use a font or an image for the VUW logo
%                          The font option will only work on ECS systems
%
\usepackage[image,ecs]{vuwproject} 

% You should specifiy your supervisor here with
\supervisor{Gideon Gouws}
% use \supervisors if there are more than one supervisor
\otherdegree{Bachelor of Engineering with Honours}
% Unless you've used the bschonscomp or mcompsci
%  options above use
%   \otherdegree{OTHER DEGREE OR DIPLOMA NAME}
% here to specify degree

% Comment this out if you want the date printed.
\date{}

\begin{document}

% Make the page numbering roman, until after the contents, etc.
\frontmatter

% %% %% %% %% %% %% %% %% %% %% %% %% %% %% %% %% %% %% %% %% %% %% %% %% %% %% %%

\begin{abstract}
  Droplet impact and evaporation presents a complex physical process worth investigating not only from a fundamental research perspective but also in its potential for industrial application. However, in order to extract usable data from this small scale, fast phenomenon in the lab producing a droplet of repeatable volume and position as well as accucartly track and collect the data (temperature, impact, evaporation) is essential in order to extract reliable and study worthy results. This procedure form the basis of this project.
\end{abstract}

% %% %% %% %% %% %% %% %% %% %% %% %% %% %% %% %% %% %% %% %% %% %% %% %% %% %% %%

\maketitle
\tableofcontents

% we want a list of the figures we defined
%\listof{fig}{Figures}

% %% %% %% %% %% %% %% %% %% %% %% %% %% %% %% %% %% %% %% %% %% %% %% %% %% %% %%

\mainmatter

% %% %% %% %% %% %% %% %% %% %% %% %% %% %% %% %% %% %% %% %% %% %% %% %% %% %% %%

\section{Introduction}
The investigation of droplet impact and evaporation is an area of experimentation of interest and application to various industry. Such as milk powder spray drying, ink jet printing, and applications of evaporative cooling.
This project will continue on from a previous instrumentation setup, evaluation its shortcomings, and design the next generation to improve the reliability and usability of the collected data. 
This report proposes a series of subsystem (re)designs to the mounting, droplet dispensing, and data collection to achieve the above goal. The project will be evaluated based on a produced report on the prior generation.

Below is a milestone based timeline, deliverables, resources and budget requirement as well as COVID-19 adaptation statement.

\section{The Problem}
This project is concerned with the development of an instrumentation rig for the study of droplet impact and drying. It is primarily/initially motivated by the powdered milk production process, specifically the behaviour of the drying and collision of concentrated milk droplets. Furthermore, the research, and developed method and procedure can be applicable to various industries. \\

To effectively investigate the behaviour, a variety of aspects can be tracked and characterised during a microscale equivalent lab process, from differing temperatures, substrates, volume, and concentrations. \\

Currently, there is an existing platform for the dispensing of droplets and data capture using high speed cameras and other various sensors. It has limitations due to manual control of starting the cameras capture and temperature capturing as well as requiring the operator to position and dispense the droplet by hand. \\

This project will, therefore, focus on the development of the third generation of this platform with the aim to design and integrate various new subsystems and evaluate their performance against the existing platform with the main project goal of having a more stable, repeatable testing platform that will not only yield more usable data but streamline the experimental process.

\subsection{Existing Process}
The current procedure as of the project beginning is a manual process. There is currently no securing bracket of any kind for the substrate sample and heater stack, the cameras and other sensors are turned on one by one and most importantly the droplet is rotated above a mark in the substrate and dispensed via syringe by hand.

The droplet then falls onto the substrate, monitored by 2 high speed cameras (profile and overhead) and the temperature of the substrate is measured via an embedded thermocouple camera a time series waveform of the experiment.

We hypothesis that this method contributes a large amount of variation into the collected data that could be masking the parameter space of interest, and limiting the granularity at which conclusions can be drawn about the process of impact and evaporation.

\newpage
\section{Proposed Solution}
The primary driving principle for both the design and evaluation of this next generation is a focus on \textit{increasing the reliability of the process by designing new and/or improving existing subsystems of the rig}. 

To be able to quantify success in that aspect and evaluations of current systems results is needed to  identify its short comings. Therefore, one of the first steps is to produce a report detailing such aspects.
\begin{itemize}
  \item Repeatability of dispensed droplet parameters (position, volume (size), contact angle) and correlate and/or see how the variation in these parameters affects the observed temperature profile and physical behaviours of the droplet throughout the evaporation process.
  \item Identify other sources of variation, such as humidity etc and their weight of influence (whether perusing a solution is worthwhile)
  \item Compare with similar solutions in the literature to gain more insight into required design consideration and constraints.
\end{itemize}

Alongside this, the first step is a mechanical design of a bracket and clamp assembly to hold and centre an aluminium heatspeader, Peltier heater, and substrate to the sample stage (fig \ref{fig::old_rig}).

From this, the primary effort will go into the droplet dispensing stage. Possibly integrating an electronic pipette and motorised stage XY  rotation to address the consistency problems. Constraints that will have to be overcome are the reduce volume capacity (syringe: ~12-15ml to max 10ml) and refilling from a reservoir.

The above represents the base deliverables, but the project may be extended with data collection automation and synchronisation, and more environmental monitoring and control.

\begin{figure}
  \begin{subfigure}{.5\textwidth}
    \centering
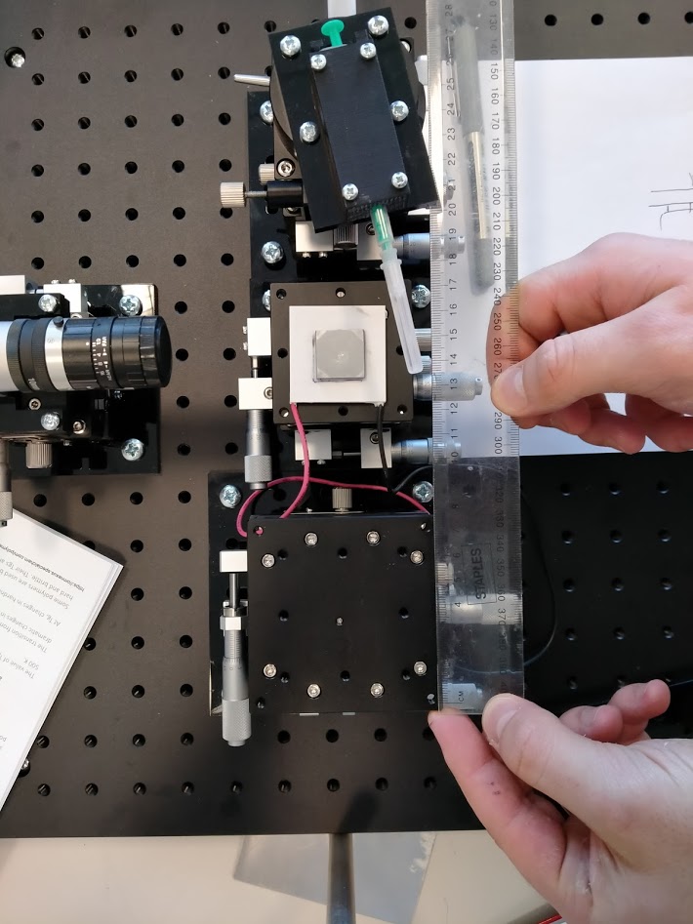
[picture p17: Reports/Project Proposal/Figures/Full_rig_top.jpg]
    
    \caption{Full Top View}
  \end{subfigure}%
  \begin{subfigure}{.5\textwidth}
    \centering
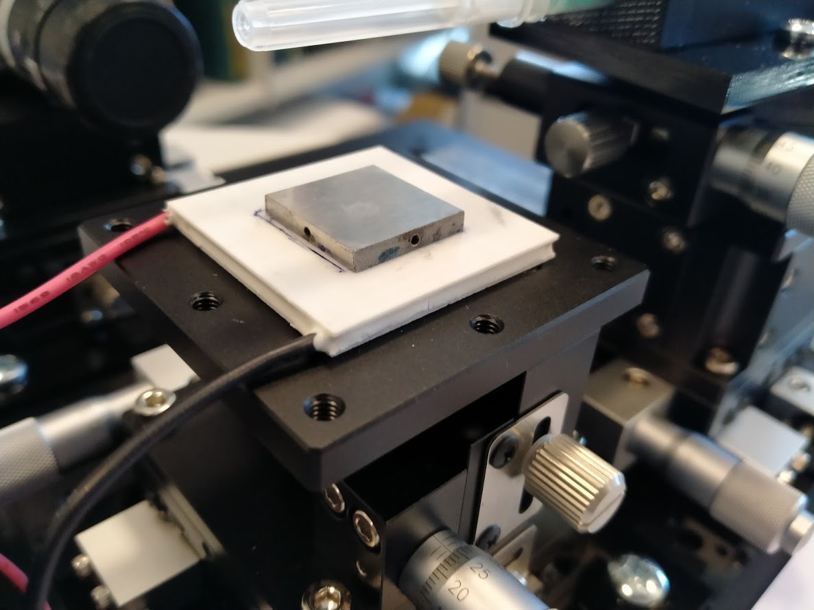
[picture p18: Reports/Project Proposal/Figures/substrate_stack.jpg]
    
    \caption{Substrate Stack close-up}
  \end{subfigure}
  \caption{Previous Rig Assembly (bar top camera)}
  \label{fig::old_rig}
\end{figure}

\subsection{Base Deliverables}
\begin{itemize}
  \item Mechanical designs to hold, centre, and clamp the substrate stack  together (1-2 weeks).
  \item Produce evaluation document based on generation 2 performance (2-3 weeks)
  \item (Main) Improved Droplet Delivery stage; dispensing control, motorised stage.
\end{itemize}

\subsection{Stretch Goals}
\begin{itemize}
  \item Synchronous data collection, i.e. cameras, temperature, droplet
  \item Measure and control environmental factors
\end{itemize}

\subsection{Timeline}
\begin{figure}[h]
  \centering
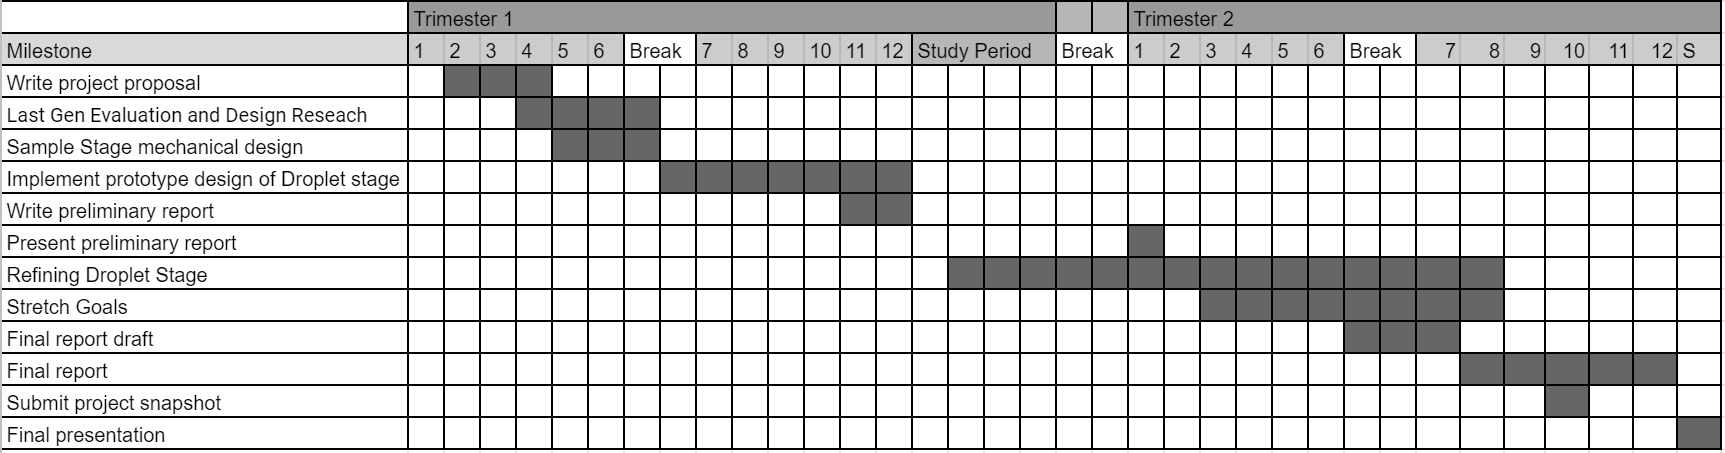
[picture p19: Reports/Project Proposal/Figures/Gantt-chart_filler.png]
  
\end{figure}

\section{Evaluating your Solution}
To evaluate the success, the produced evaluation document on generation 2 will serve as the primary comparison. Each subsystem; mechanical brackets, droplet dispensing, temperature measurements will be tested individually to quantise their contribution and as a gradually integrated whole.

The preliminary evaluation criteria (subject  to change with the discretion of the previous generation analysis) include consistency and repeatability of the following:
\begin{itemize}
  \item Dispensed volume
  \item Impact characteristics (centre, angle, etc)
  \item Uncontrolled temperature variation
\end{itemize}

\section{Resource Requirements}

\subsection{Facilities and Tools}
\begin{itemize}
  \item Labs AM219 and LB207
  \item Computer with SolidWorks, LabView, and other data processing tools
  \item Electronics Test bench (PSU, signal generator, scope etc)
  \item Access to fabrication workshop
\end{itemize}

\subsection{Health and Safety}
The project does not necessitate
\begin{itemize}
  \item Lab Induction (LM207)
  \item Peltier Heaters
  \item Basic electronic safety
\end{itemize}

\subsection{Budget}
It is worth noting that the instrumentation platform is largely constructed with all its major components, and most needed parts for the design and development of the project are already present.

Given this, the project has estimated a budgetary restriction of \$400.
\begin{itemize}
  \item \$200 to cover workshop manufacturing costs of mechanical designs
  \item \$200 for the purchase of stepper motors and auxiliary components, PCB design and manufacture and all other electronic component costing.
\end{itemize}

\section{COVID-19 Alert Level Management}
The combat and alleviate the effects of increased alert levels, the collaborative design and physical work (bracket design and manufacture etc) will be front loaded or at the very least prepared for. In the event of restricted access to the university, the project can shift to tasks more remote friendly with some ease. Such as more development of data collection software and syncing as well as EDA design of say, the motorised stage circuitry. Meetings can be remotely undertaken without effort and all files, material and supporting information is being stored and synced via git and other remote storage solutions.

If the circumstance allows it, equipment may also be taken home and work can be done at an at-home workshop. 

% %% %% %% %% %% %% %% %% %% %% %% %% %% %% %% %% %% %% %% %% %% %% %% %% %% %% %%
\backmatter
% %% %% %% %% %% %% %% %% %% %% %% %% %% %% %% %% %% %% %% %% %% %% %% %% %% %% %%

% \nocite{*}
% \bibliographystyle{ieeetr}
% \bibliography{sample}
\end{document}

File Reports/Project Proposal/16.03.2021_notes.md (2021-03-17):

# applications
* ink jet printing
* food, spray drying
* evaporative cooling
* etc

Should I put the experimental process in the proposal?
Dropping, 2 cameras (X, Z), substrate temperate (timeseries)
yes

Workshop budget: 
* 200 substrate frame
* Stepper motors and auxiliary

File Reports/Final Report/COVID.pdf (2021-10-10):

Due to the nature of this project, being integrated into a heavy immovable optical breadboard and requiring specific equipment and resources (LabVIEW, NI DaQs, PSU etc). The COVID-19 lockdown of Aug-2021 meant that aspects of the project that were intended to implemented, just could not be. These included a fuller LabVIEW interface and auto homing feature.

The timing of the lockdown occurred right as the project was entering its integration evaluation period and restricted the time available to collect and analyse more data. Additionally, not every part arrived for full PCB assembly so evaluation had to be partially done on the breadboard prototype.

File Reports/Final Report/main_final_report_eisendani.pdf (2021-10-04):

# VICTORIA UNIVERSITY OF WELLINGTON

Te Whare Wananga o te ¯ | Upoko o te Ika a M ¯ | aui ¯

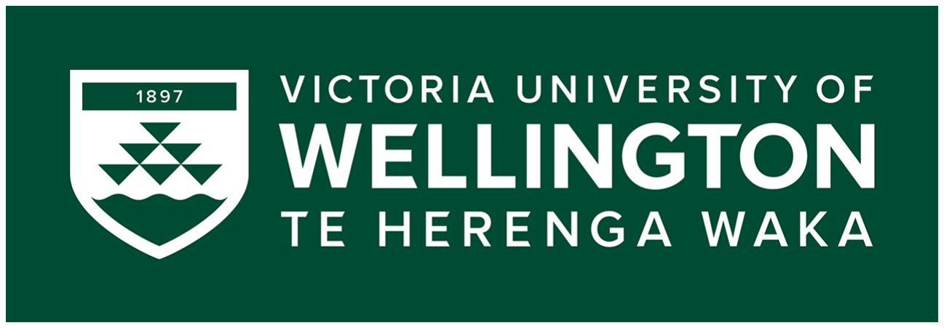
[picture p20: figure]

# School of Engineering and Computer Science

Te Kura Matai P ¯ | ukaha, P ¯ | urorohiko ¯

PO Box 600
Wellington
New Zealand

Tel: +64 4 463 5341
Fax: +64 4 463 5045
Internet: office@ecs.vuw.ac.nz

## Instrumentation System for Liquid Drop Impact and Evaporation

| Daniel Eisen

Supervisor: Dr. Gideon Gouws

Submitted in partial fulfilment of the requirements for Bachelor of Engineering with Honours.

Abstract

//TODO rewriting
Droplet impact and evaporation presents a complex physical process worth investigating not only from a fundamental research perspective but also in its potential for industrial application. However, in order to extract usable data from this small scale, fast phenomenon in the lab producing a droplet of repeatable volume and position as well as accucartly track and collect the data (temperature, impact, evaporation) is essential in order to extract reliable and study worthy results. This procedure form the basis of this project. This projects approach is to add motorised automation to droplet dispensing with aims to control for droplet volume, positional variation, contact angle and speed up the procedure and allow for greater flexibility in the experimental process.

# Contents

1 Introduction | 1
1.1 Motivation | | 1
1.2 Goals | | 1
2 Background and Related Work | 2
2.1 Instrumentation and the Experiment | | 2
2.2 Background on Stepper motor control | | 2
2.3 Other Approaches | | 2
3 Inital Evaluation | 4
3.1 Current Experimental Setup | | 4
3.2 Repeatability and Reliability | | 4
3.3 Revised Approach | | 4
4 Design | | 7
4.1 Project Specifications and Justifications | | 7
4.2 System Overview | | 7
4.3 Mechanical Design | | 7
4.3.1 | Rotating Pipette Mount | | 7
4.3.2 | Z micrometer Control | | 8
4.4 Electronic Design | | 8
4.4.1 | Motor Driving | | 8
4.4.2 | Pipette Triggering | | 8
4.4.3 | Environmental Monitoring | | 9
5 Implementation | 10
5.1 Mechanical Design | | 10
5.1.1 | Rotating Pipette Mount | | 10
5.1.2 | Z micrometer Control | | 10
5.2 Software | | 10
5.2.1 | Motorised Dispensing Controller | | 10
5.2.2 | Environmental Monitor | | 10
5.2.3 | LabView Temperature Logger | | 10
5.3 Electronic Design | | 10
5.3.1 | Motor Driving | | 11
5.3.2 | Setup and Requirements | | 11
5.3.3 | Results | | 11
5.3.4 | Pipette Triggering | | 11
5.3.5 | Environmental Monitoring | | 11

6 Evaluation | | 12
6.1 Mechanical Stability | | 12
6.1.1 | Procedure | | 12
6.2 Droplet Volume | | 12
6.2.1 | Results | | 12
6.3 Repeatability and Reliability | | 12
6.3.1 | Procedure | | 13
6.3.2 | Analysis | | 13
7 Conclusions and Future Work | 14
7.1 Conclusion | | 14
7.2 Future Work | | 14

# Chapter 1: Introduction

//TODO re-write in progress

### 1.1 Motivation

The investigation of droplet impact and evaporation is an area of interest and application to various industries. Examples of these include milk powder spray drying, ink jet printing, and applications of evaporative cooling. This project will continue on from a previous instrumentation setup, evaluating its shortcomings, and designing the next generation. This will improve the reliability and usability of the collected data from the previous setup, and introduce methods of automating the process.
Applications of interest
- Spray cooling
- powder (Milk) manufacture
- ink-jet printing

### 1.2 Goals

Goal: To characterise behaviour of a droplet impacting and evaporating from a given substrate.

- Increase Repeatability and Reliability of results
- Increase usability of process via automation
- Produce Extendible platform that can be built upon beyond this projects scope

# Chapter 2: Background and Related Work

### 2.1 Instrumentation and the Experiment

Cover consideration with this kind of instrumentation/experimental measurement system and how it applied to this experimental application.

### 2.2 Background on Stepper motor control

//TODO more passes for clarity.
This section will cover the background of controlling bipolar stepper motors via a step/direction style driver setup, as its concepts will be mentioned later in the report. This is a focused background on the key considerations and requirements when designing for and operating this specific subset, and by no means applicable to all driving and specific motor choices.
The stepper motors provide precise positioning and are capable of moving their rotor to a specified position and holding that position at a wide range of load torques. This capability makes the stepper motors popular in optics, medical instruments, factory automation, and industrial equipment.
The typical topology of a stepper driving system (based around the step/direction method) consists of a controller, driver, and stepper motor. The controller provides a direction signal and step pulses, while the driver converts these signals into actual electrical power and supplies them to the motor. The stepper motor moves in steps, each step covering one step angle, which can be described as the rotor displacement corresponding to one step pulse [1]. Stepper motors typically have a step size specification (e.g. 1.8° or 200 steps per revolution), which applies to full steps. Step/direction drivers usually provide a ’microstepping’ mode which increases the resolution by allowing intermediate step locations, which are achieved by energising the coils with intermediate current levels [2].
The last major consideration in driving steppers is controlling the start-up and stopping speeds for the controller’s provided pulse train to the driver. As the motor is a mechanical device in the real world, expecting a perfect impulse response will lead to driving failure. Inertia ratio is critical to stepper motor acceleration [2]. Too great a difference in inertia ratio between system and motor risks missed steps or stalling the coils. So when starting a stepper motor, acceleration and deceleration should happen through pulses to the motor that start slowly and gradually quicken in a process called ramping.

### 2.3 Other Approaches

//TODO: Go into greater detail to add context in the field of droplet instrumentation.
In literature, there exists a variety of rigs for similar experiments. These were explored to gauge a range of what factors were controlled (and measured) and with what approaches. In summary:

- Controlled environmental factors with basic box [2] or measured factors only [3].
- Controlled for droplet position and volume with hard mounted pump plus needle, but lacks environmental control or automation, and there is no top view camera [4] [5].
- Incorporated stepper motor driven automation, but no environmental control or monitoring [6].
- Full environmental chamber and fixed droplet pump, but single camera, has separate uncontrolled rig for top view [7].

# Chapter 3: Inital Evaluation

### 3.1 Current Experimental Setup

The instrumentation as exists is assembled with an optical breadboard and XYZ+R stages with micrometre controls. A central stage holds the substrate with internally mounted thermocouple. Two manual focus cameras are positioned in profile and top down views, and the droplet is dispensed manually via a syringe mounted horizontally to a XYZ+R stage. The current procedure is a manual process. The syringe tip is rotated above a marked point on the substrate, and hand emptied and refilled. This results in volume and positional variation between runs. This procedural variance is the focus of this project.

### 3.2 Repeatability and Reliability

Data taken from a series of five droplet runs was analysed to extract the variety in droplets and its effect on the measure temperature profile.

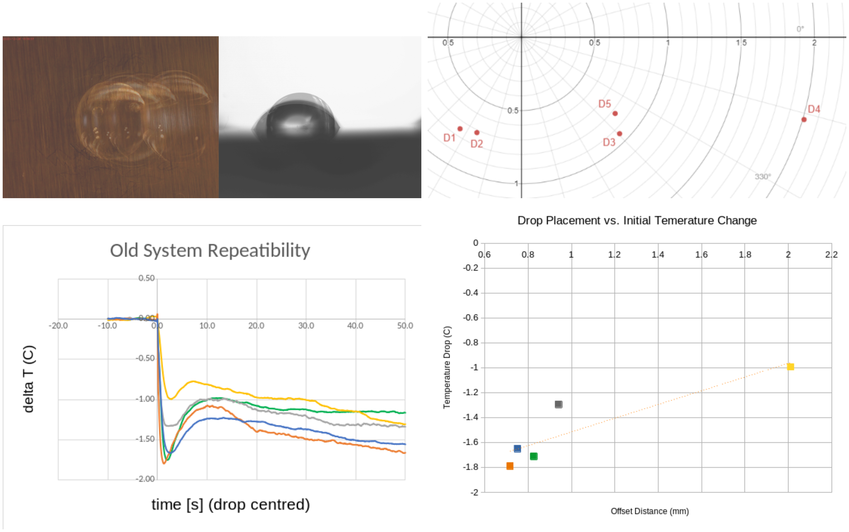
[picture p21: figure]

### 3.3 Revised Approach

The focus of the project is now twofold. Firstly on the automation of the process to allow for faster, pre-programmed runs to be carried out easier, and secondly to improve on the repeatability and reliability of the results by controlling the procedural factors of the experiment.

Droplet | Distance from Centre (mm) | Estimated Volume (mmˆ2)
1 | 0.7506 | 16.55
2 | 0.7164 | 17.91
3 | 0.9402 | 17.89
4 | 2.0104 | 17.57
5 | 0.8258 | 16.21
| Distance from Mark | Measured Temperature Drop
Min Pos Offset | 0.71mm | -1.7901◦C
Max Pos Offset | 2.01mm | -0.9944◦C
| Volume | Contact Angle
Shape Variance | 0.629mm³ | 25.894 degrees †

Table 3.1: Variance in Setup

†This excluded an outlier of an almost spherical droplet with contact angles exceeding 95 degrees. This large variation is most likely due to inconsistency in surface chemisty from washing.

An electronic pipette will be used to dispense a precise volume, and motorised stages will be used to provide preprogrammed, repeatable motion. The environmental factors however are not to be ignored, though controlling them is outside of the scope of this project. They will, however, be monitored, and this project will implement data collection of temperature, atmospheric pressure and humidity so these factors can be correlated to any remaining variation in data. w

Effector | Likelihood Effect Strength
Position
Volume
Contact angle*
Humidity
Temperature
Pressure

# Chapter 4: Design

### 4.1 Project Specifications and Justifications

The design process uses the goals of the experiment and the results of the initial evaluation to inform what and how various subsystems are designed.
From this there is a number of requirements to consider:
- Mechanical Stability:
- System Expandability:

### 4.2 System Overview

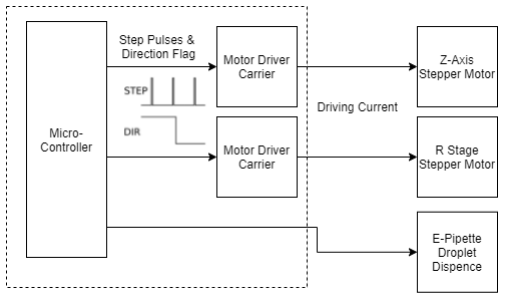
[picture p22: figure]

### 4.3 Mechanical Design

- Discuss requirements for minimising settling time, vibrations, oscillations.overshoot of the pipette motion

### 4.3.1 Rotating Pipette Mount

- 3D printed pipette clamp
- Laser cut Tower mounted
- motor interface and stage fastening

### 4.3.2 Z micrometer Control

- Requirements: micrometer motion/extension as its turn
- Sliding motor shaft to knob required (2 passed)
- How it imposed restrictions on the system (freedom of motion)

### 4.4 Electronic Design

### 4.4.1 Motor Driving

The Requirements

To drive the selected stepper motors, discrete step/direction style micro stepping drivers were chosen. This allows for the design to be flexible with its electronics placed to accommodate the experimental needs. Allows for a fairly agnostic choice for controller to supply the control signals, and standardised pinouts allow for requirement flexibility and replacements.

| A4988 | DRV8825 | STPIN820 | DRV8834
Step Res | 1/16 | 1/32 | 1/256 | 1/32
Logic Level | 3V3/5V | 3V3/5V | 3V3/5V | 3V3/5V
Current Limit | 1A | 1.5A | 0.9A | 1.5A
Drive Voltage | 8-35V | 8.2-45V | 7-48V | 2.5-10.8

Table 4.1: Comparison of considered drivers

Main consideration for device choice are: micro step resolution, driving current limit (passively cooled), and configuration pinout.

The Choice

The DRV8825 was ultimately chosen.

- High microstepping resolution, lower than the STPIN820 but cheap high resolution driver are prone to step skipping [2]
- Highest driving current as torque requirements are unknown for this design the headroom is nice even if it isn’t use, especially as it will run cooler at lower power draw.
- It ranked above the DRV8834 due to it configuration pins (to set microstepping mode) as it provide all 3 pins without the requirement to leave pins floating as a setting thus allowing for full software control.

### 4.4.2 Pipette Triggering

//TODO maybe move to implementation

- Signal requirements that lead to a trigger environmental
- interfacing the controller with the board

### 4.4.3 Environmental Monitoring

- What will be measured?
- Power (battery?)
- Sleep the conserve

# Chapter 5: Implementation

//TODO rename sections to reflect work done

### 5.1 Mechanical Design

- Go into 3d printing/laser cutting refinement, testing and adjustment
- Tolerance and dimension adjustment
- Noted changed and drawback from design

### 5.1.1 Rotating Pipette Mount

### 5.1.2 Z micrometer Control

- Note initially large vibrations as z decreases, caused be loose tolerance, too small coupler. Caused droplet to prematurely detach at larger values.

### 5.2 Software

//Insert Serial Command Table (maybe only appendix)

### 5.2.1 Motorised Dispensing Controller

ESP32 based system controller with serial interface for issuing commands. Provides functionality to:

- Motorised stages, height and angular position
- e-Pipette droplet dispensing

### 5.2.2 Environmental Monitor

- Auto sleeping, button wake upon
- Circuit-Python implementation

### 5.2.3 LabView Temperature Logger

### 5.3 Electronic Design

- full circuit
- pcb
- any and all adjustment found and made during implementation

### 5.3.1 Motor Driving

### 5.3.2 Setup and Requirements

- characterised skipping issue at 100Hz, 180Hz-200hz in single step
- implemted micro stepping to solve

//TODO rewrite
Driving firmware was implemented on an ESP32 to validate its ability in producing the required pulse train step signal. The controller was required to produce N steps (pulses) at a set average speed, and ramp up and down that pulse speed at the head and tail of that signal.
Set values of 200 steps forward and back, at a speed of 200 steps per second, with max acceleration or 800 steps per second per second:
These pulses were captured on a second microcontroller listening for falling edges to trigger an interrupt routine to record and display that data.

### 5.3.3 Results

Figure 5.1:a shows a successfully produced signal of 200 pulses with an inferred acceleration at its head/tail. This speed ramping is better illustrated in figure 5.1:b showing the stepping change in pulses per second over the course of the pulse train.

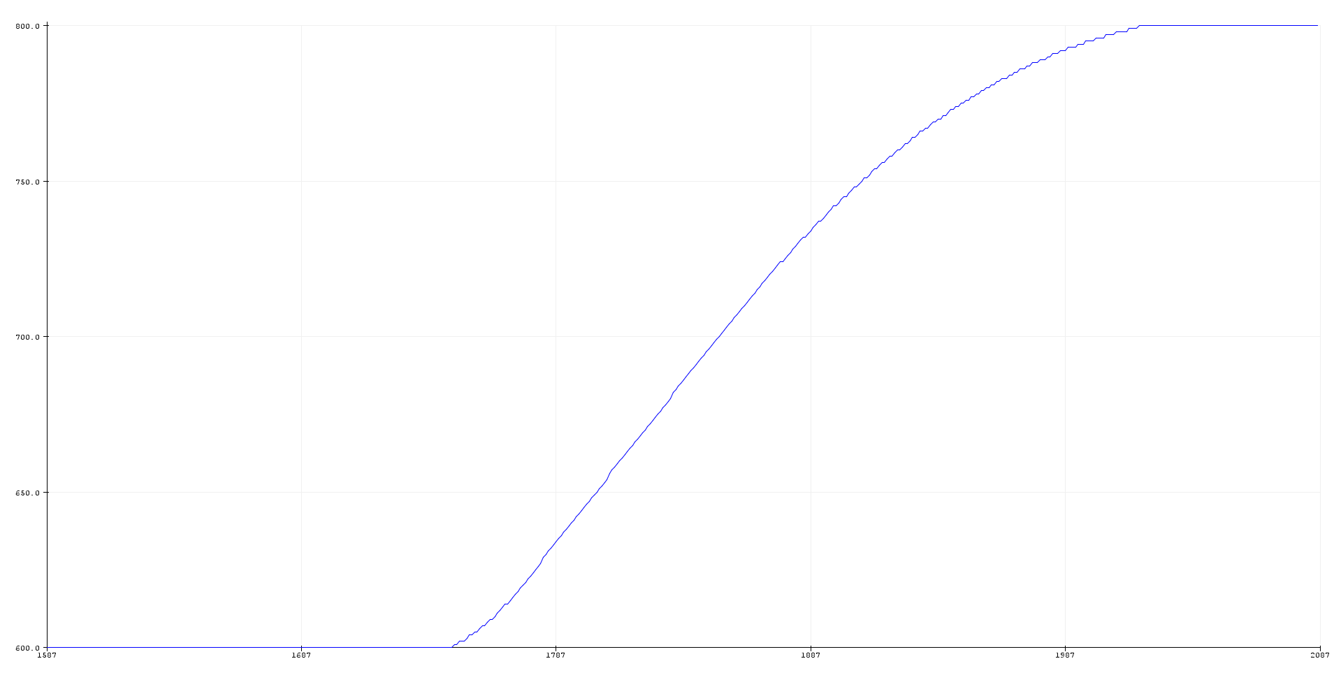
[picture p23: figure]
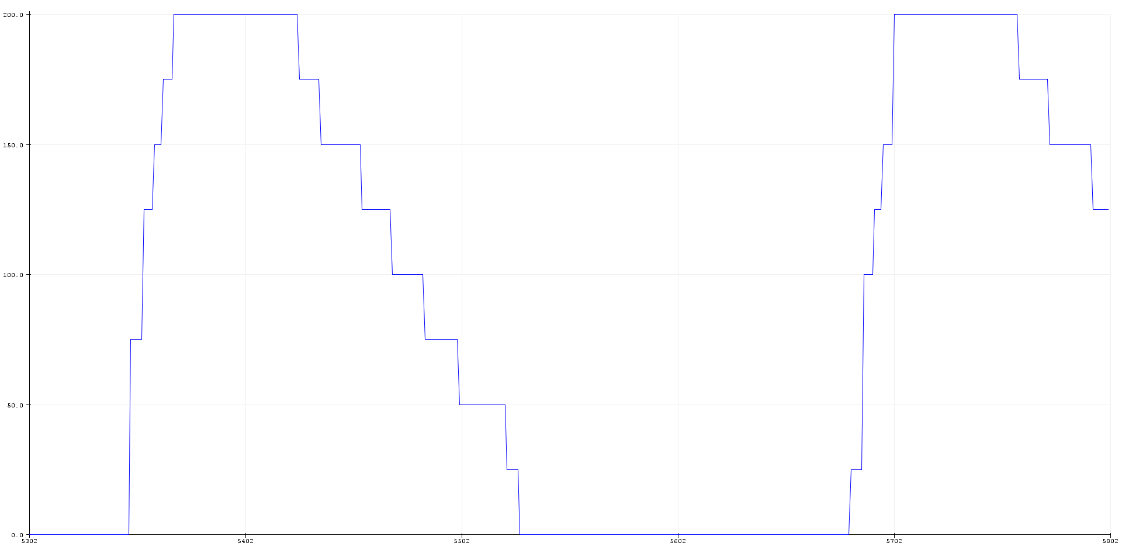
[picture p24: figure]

(a) Pulse Count | (b) Pulses per Second

Figure 5.1

### 5.3.4 Pipette Triggering

//TODO

### 5.3.5 Environmental Monitoring

//TODO

# Chapter 6: Evaluation

### 6.1 Mechanical Stability

Perform Motor driving parameter sweep to optimise mechanical performance according to requirements; of minimising pipette tip overshoot and settling time.

### 6.1.1 Procedure

- Position tip at -1/4 revolution before zero point
- Set Speed/acceleration values
- Swing to zero position
- Repeat for value sleep=1rev/s, acc=1/rev/s/s → speed=2rev/s, acc=10/rev/s/s
- Note: acceleration is the ramp down at end/start of motion so is what we care most about
- Camera captured motion

### 6.2 Droplet Volume

Something the previous system could not achieve was dispensing a variety of volumes. Use e-pipettes programmable volume to investigate the limits of this project.

- How large a droplet can be held on to? (prelim: 8uL)
- How large (over above) can reliably self release (w/out touch down)
- How small a droplet can be dispensed (e-pipette has draw-back).

### 6.2.1 Results

//insert generated figures of tip position
//generated trend lines/aggregated data (settle, overshoot) from data.

### 6.3 Repeatability and Reliability

This section aims to produce the main set of comparable results for evaluating the projects produced system against the output of the previous setup. Thus justifying the success of one of main goals.

### 6.3.1 Procedure

- Initial Setup: Roughly Position substrate stage, reservoir platform and note angular positions as well as vertical clearance requirements.
- Zero System: Using overhead camera precisely position pipette tip above substrate centre
- Data Acquisition: Initialise cameras, collect pixel:mm calibration data for analysis, initial LabView temperature logger, and environmental monitor noted. Info: temperature data rate, camera frame rate
- Automated Sequence: Via the serial link, enter the procedures command sequence to represent → lower, draw up fluid, raise, position over substrate, dispense, lower, raise, clear camera view. With appropriate delays.
- Capture: Begin data collection and automated dispense.
- Repeat: Minimum of 5 times. Each time carefully cleaning substrate surface to minimised up measured factors.

### 6.3.2 Analysis

To show the system successfully increases the consistency of droplet position,

# Chapter 7: Conclusions and Future Work

Future work should not just be a list of things that you would have done if you had a little more time. Talk about new things that are possible now that you have finished your project. What projects could an ENGR489 student tackle next year if they started from your end point?

### 7.1 Conclusion

### 7.2 Future Work

# Bibliography

[1] “Implementing a step-direction interface-based stepper motor controller,” Application Note AC413, pp. 1–9, 2014.
[2] “Stepping motors and their microprocessor controls, second edition takashi kenjo & akira sugawara, 1994 oxford, oxford university press isbn 0 19 859385 6,” European Journal of Engineering Education, vol. 20, no. 3, pp. 386–386, 1995.
[3] E. Gatapova, A. Semenov, D. Zaitsev, and O. Kabov, “Evaporation of a sessile water drop on a heated surface with controlled wettability,” Colloids and Surfaces A Physicochemical and Engineering Aspects, vol. 441, pp. 776–785, 01 2014.
[4] J. H. Moon, D. Kim, and S. Lee, “Spreading and receding characteristics of a nonnewtonian droplet impinging on a heated surface,” Experimental Thermal and Fluid Science, vol. 57, 09 2014.
[5] P. Hanichen, A. Bender, B. Voß, T. Gambaryan-Roisman, and P. Stephan, “Drop evap- ¨ oration of hydrocarbon fluids with deposit formation,” International Journal of Heat and Mass Transfer, vol. 128, pp. 115–124, 01 2019.
[6] M. Frasao, A. Oliveira, and R. Gonc¸alves dos Santos, “Determination of nukiyama and ˜ leidenfrost temperatures for hydrocarbons using the droplet evaporation method,” 03 2018.
[7] S. David, K. Sefiane, and L. Tadrist, “Experimental investigation of the effect of thermal properties of the substrate in the wetting and evaporation of sessile drops,” Colloids and Surfaces A: Physicochemical and Engineering Aspects, vol. 298, pp. 108–114, 04 2007.

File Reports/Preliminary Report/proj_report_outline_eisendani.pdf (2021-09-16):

# VICTORIA UNIVERSITY OF WELLINGTON

Te Whare Wananga o te ¯ | Upoko o te Ika a M ¯ | aui ¯


# School of Engineering and Computer Science

Te Kura Matai P ¯ | ukaha, P ¯ | urorohiko ¯

PO Box 600
Wellington
New Zealand

Tel: +64 4 463 5341
Fax: +64 4 463 5045
Internet: office@ecs.vuw.ac.nz

## Instrumentation System for Liquid Drop Impact and Evaporation

| Daniel Eisen

Supervisor: Gideon Gouws

Submitted in partial fulfilment of the requirements for Bachelor of Engineering with Honours.

Abstract

Droplet impact and evaporation presents a complex physical process worth investigating not only from a fundamental research perspective but also in its potential for industrial application. However, in order to extract usable data from this small scale, fast phenomenon in the lab producing a droplet of repeatable volume and position as well as accucartly track and collect the data (temperature, impact, evaporation) is essential in order to extract reliable and study worthy results. This procedure form the basis of this project. This projects approach is to add motorised automation to droplet dispensing with aims to control for droplet volume, positional variation, contact angle and speed up the procedure and allow for greater flexibility in the experimental process.

# Contents

1 Introduction | 1
2 Background | 2
2.1 Current Experimental Setup | | 2
2.2 Other Approaches | | 2
2.3 Background on Stepper motor control | | 3
2.4 Revised Approach | | 3
3 Work Completed | 4
3.1 Substrate Mounting | | 4
3.2 Pipette and Mechanical Mounting | | 4
3.2.1 | Interactions and Difficulties | | 5
3.3 Electronic Design and Part Selection | | 5
3.3.1 | Motor | | 5
3.3.2 | Motor Drivers | | 6
3.3.3 | Auxiliary Components | | 6
3.4 Initial Driving Firmware Implementation | | 7
3.4.1 | Setup and Requirements | | 7
3.4.2 | Results | | 7
4 Future Plan | | 8
4.1 Work to be Completed | | 8

i

# Chapter 1: Introduction

The investigation of droplet impact and evaporation is an area of interest and application to various industries. Examples of these include milk powder spray drying, ink jet printing, and applications of evaporative cooling. This project will continue on from a previous instrumentation setup, evaluating its shortcomings, and designing the next generation. This will improve the reliability and usability of the collected data from the previous setup, and introduce methods of automating the process.
This preliminary report covers the key problem of the experimental setup that the project aims to improve, and identifying the main factors that can introduce variation into the results. It will also provide an overview and evaluation of the current and previous systems, and the variability of their results, including possible sources of these inconsistencies. It will briefly cover other similar systems in literature, and what they control and how. Then the report will redefine the project scope, its objectives, and what variables it aims to control and how. Finally, it will cover what work has been done and where the current progress and results stand, as well as detailing difficulties and decisions made along the way.

### The Experiment

A droplet of liquid (concentrated milk, water, or similar) is deposited on a heated substrate (stainless steel, copper, or glass). The temperature of the substrate is monitored. The progression of the droplet’s impact and evaporation is captured by two cameras; above and profile view. This produces a multidimensional perception of the developing behaviour and characteristics of the droplet over time. This usually takes between 1 and 2 minutes per droplet.

Problems

This experiment relies on the precise placement of a droplet above a temperature sensor, in a set focal plane, to measure the droplet as it progresses through it’s evaporation. Therefore, it can be said there exists uncontrolled factors that can alter the results, affecting the final values and the repeatability of the experiment. These factors can be separated into environmental and procedural sources.

Environmental | Procedural
Humidity | Droplet Volume
Atmospheric Pressure | Droplet Position (Rel. to thermocouple)
Temperature | Contact Angle (contact surface area)

# Chapter 2: Background

### 2.1 Current Experimental Setup

The instrumentation as exists is assembled with an optical breadboard and XYZ(R) stages with micrometre controls. A central stage holds the substrate with internally mounted thermocouple. Two manual focus cameras are positioned in profile and top down views, and the droplet is dispensed manually via a syringe mounted horizontally to a XYZ+R stage. The current procedure is a manual process. The syringe tip is rotated above a marked point on the substrate, and hand emptied and refilled. This results in volume and positional variation between runs. This procedural variance is the focus of this project.

| Distance from Mark | Measured Temperature Drop
Min Pos Offset | 0.71mm | -1.7901◦C
Max Pos Offset | 2.01mm | -0.9944◦C
| Volume | Contact Angle
Shape Variance | 0.629mm³ | 25.894 degrees †

Table 2.1: Variance in Setup

†This excluded an outlier of an almost spherical droplet with contact angles exceeding 95 degrees. This large variation is most likely due to inconsistency in surface chemisty from washing.

Data taken from a series of five droplet runs was analysed to extract the variety in droplets and its effect on the measure temperature profile.

### 2.2 Other Approaches

In literature, there exists a variety of rigs for similar experiments. These were explored to gauge a range of what factors were controlled (and measured) and with what approaches. In summary:

- Controlled environmental factors with basic box [1] or measured factors only [2].
- Controlled for droplet position and volume with hard mounted pump plus needle, but lacks environmental control or automation, and there is no top view camera [3] [4].
- Incorporated stepper motor driven automation, but no environmental control or monitoring [5].
- Full environmental chamber and fixed droplet pump, but single camera, has separate uncontrolled rig for top view [6].

### 2.3 Background on Stepper motor control

This section will cover the background of controlling bipolar stepper motors via a step/direction style driver setup, as its concepts will be mentioned later in the report. This is a focused background on the key considerations and requirements when designing for and operating this specific subset, and by no means applicable to all driving and specific motor choices.
The stepper motors provide precise positioning and are capable of moving their rotor to a specified position and holding that position at a wide range of load torques. This capability makes the stepper motors popular in optics, medical instruments, factory automation, and industrial equipment.
The typical topology of a stepper driving system (based around the step/direction method) consists of a controller, driver, and stepper motor. The controller provides a direction signal and step pulses, while the driver converts these signals into actual electrical power and supplies them to the motor. The stepper motor moves in steps, each step covering one step angle, which can be described as the rotor displacement corresponding to one step pulse [7]. Stepper motors typically have a step size specification (e.g. 1.8° or 200 steps per revolution), which applies to full steps. Step/direction drivers usually provide a ’microstepping’ mode which increases the resolution by allowing intermediate step locations, which are achieved by energizing the coils with intermediate current levels [1].
The last major consideration in driving steppers is controlling the start-up and stopping speeds for the controller’s provided pulse train to the driver. As the motor is a mechanical device in the real world, expecting a perfect impulse response will lead to driving failure. Inertia ratio is critical to stepper motor acceleration [1]. Too great a difference in inertia ratio between system and motor risks missed steps or stalling the coils. So when starting a stepper motor, acceleration and deceleration should happen through pulses to the motor that start slowly and gradually quicken in a process called ramping.

### 2.4 Revised Approach

The focus of the project is now twofold. Firstly on the automation of the process to allow for faster, pre-programmed runs to be carried out easier, and secondly to improve on the repeatability and reliability of the results by controlling the procedural factors of the experiment.
An electronic pipette will be used to dispense a precise volume, and motorised stages will be used to provide preprogramed, repeatable motion. The environmental factors however are not to be ignored, though controlling them is outside of the scope of this project. They will, however, be monitored, and this project will implement data collection of temperature, atmospheric pressure and humidity so these factors can be correlated to any remaining variation in data.

# Chapter 3: Work Completed

### 3.1 Substrate Mounting

The proposal initially outlined the design of a mount/fastener for the substrate stack, to integrate a heat spreader, and to better ensure centering and thermocouple placement. Initial meetings with the on-site workshop and design started early with rough sketch designs and discussions on material and manufacture. However, it was quickly decided that focus should be shifted elsewhere in the project and this be returned to at a later date if needed, as the substrate is a shared component of the two projects centred around this experimental setup, and the development new droplet dispensing was the true focus of this project.

### 3.2 Pipette and Mechanical Mounting

Given the decision for the new rig to be centred around an electronic pipette, as opposed to the manual syringe, a new mounting assembly was needed to secure the pipette to the XYZ stage, ensure there is minimal play and backlash, and position its tip above the substrate for droplet dispensing.
Requirements: The pipette had to be held at 150mm from the top of the optical stage, at 36 degrees. Finer adjustments to be made with the XYZ micrometre controls.
A tower [3.1] was designed as the mounting solution. It was constructed from laser cut 6mm acrylic as it had been successfully used in other parts of the existing rig, could be very quickly manufactured to allow rapid prototyping, and producing of a variety of mounting points and different plates. Assembly was left open to allow for access and modification. A taller than final tower design was cut to allow for the new procedure to be carried out before the motorised system was complete.


(a) Unassembled Tower | (b) CAD Design | (c) Tower Assembled

Figure 3.1: Pipette Tower

### 3.2.1 Interactions and Difficulties

The electronic pipette formfactor is very ’organic’, so the clamping mechanism to fit it to the tower plate itself was challenging to design to successfully restrict its rotation and backlash. The base design used to accomplish this was a 3D-printed ring clamp [see 3.1:a] meant to be tightened and fit to the unique form of the pipette body. A variety of ring sizes and gap distance were printed and test fitted. From this I determined that a ring diameter of 32mm and a gap of 6mm fits and deforms to the shape of the pipette. However, there was still some rotation and slip so a notch was cut into the acrylic to slot the pipettes support rest and a second ring clamp attached lower down of the body.

### 3.3 Electronic Design and Part Selection

The electronic design for this project is as follows: A microcontroller provides control signals to step/direction drivers for two stepper motors. One stepper motor controls the tower rotation and the other the optical stage z-axis. The controller also interfaces with the electronic pipette to trigger a droplet release.


Figure 3.2: Block Diagram of Base Electronic Design

### 3.3.1 Motor

The motion required for the motors in this system is to provide rotation about the vertical axis to the mounted pipette, to swing from above the substrate to out of the camera view and over a refill reservoir, as well as continuous rotation to interface the Z axis control for droplet depositing and possible refilling.
Stepper motors allow for both precise position control without the need for a feedback system and are capable of continuous rotation. In comparison, brushed/brushless DC motors require encoders for positional control and servos may do either but not both continuous rotation and positioning.
NEMA17 standard sized steppers were chosen to best fit the dimensions of the XYZ optical stage (60mm plate to 40mm motor frame) with room for fastening hardware. That left two choices for the top R stage motor; full size 38mm high frame or shorter pancake frame. Even through the pancake frame would reduce the overall height of the system, the shaft length available for this motor is less only 7mm and would greatly restrict the mounting options of the tower to the motor. For this reason 2 NEMA17x38mm Stepper motors were chosen.

### 3.3.2 Motor Drivers

The Requirements

To drive the selected stepper motors, I decided on discrete step/direction style micro stepping drivers. This allows for the design to be flexible with its electronics placed to accommodate the experimental needs. Allows for a fairly agnostic choice for controller to supply the control signals, and standardised pinouts allow for requirement flexibility and replacements.

| A4988 | DRV8825 | STPIN820 | DRV8834
Step Res | 1/16 | 1/32 | 1/256 | 1/32
Logic Level | 3V3/5V | 3V3/5V | 3V3/5V | 3V3/5V
Current Limit | 1A | 1.5A | 0.9A | 1.5A
Drive Voltage | 8-35V | 8.2-45V | 7-48V | 2.5-10.8

Table 3.1: Comparison of considered drivers

Main consideration for device choice are: micro step resolution, driving current limit (passively cooled), and configuration pinout.

The Choice

The DRV8825 was ultimately chosen.

- High microstepping resolution, lower than the STPIN820 but cheap high resolution driver are prone to step skipping [1]
- Highest driving current as torque requirements are unknown for this design the headroom is nice even if it isn’t use, especially as it will run cooler at lower power draw.
- It ranked above the DRV8834 due to it configuration pins (to set microstepping mode) as it provide all 3 pins without the requirement to leave pins floating as a setting thus allowing for full software control.

### 3.3.3 Auxiliary Components

In addition to the above primary components lever-action limit switches were also selected if it were to be deemed necessary for the motor controller to have that kind of positional feedback for homing and the like. Shaft mounting hardware was also purchased.

### 3.4 Initial Driving Firmware Implementation

### 3.4.1 Setup and Requirements

With the parts selected and ordered, I wrote test firmware on an ESP32 to validate its ability in producing the required pulse train step signal. The controller was required to produce N steps (pulses) at a set average speed, and ramp up and down that pulse speed at the head and tail of that signal.
Set values of 200 steps forward and back, at a speed of 200 steps per second, with max acceleration or 800 steps per second per second:
These pulses were captured on a second microcontroller listening for falling edges to trigger an interrupt routine to record and display that data.

### 3.4.2 Results

Figure 3.3:a shows a successfully produced signal of 200 pulses with an inferred acceleration at its head/tail. This speed ramping is better illustrated in figure 3.3:b showing the stepping change in pulses per second over the course of the pulse train.


(a) Pulse Count | (b) Pulses per Second

Figure 3.3

Upon the arrival of the motors themselves it will be determined what the exact requirements for this signal will be to prevent coil stalling and reduce vibrations in the system. It does however leave me with 3 main variables to tune this performance:

- Constant Step Count: What level of micro stepping can be achieved/whether it is required
- Step speed: Limits, usable speeds, stability
- Step Acceleration: Motor performance, stall avoidance, resonances

# Chapter 4: Future Plan

Now that parts have arrived for a base deliverable prototype. Electronics can be assembled into rig, power and driving requirements can be properly determined and the new automated process can be tested and refined.

### 4.1 Work to be Completed

1. Assemble first motorised version (Immediately-2Wks)
- Recut tower to new height
- Mount R stage stepper to stage and tower
- Design sliding shaft coupler for z stage micrometre
2. Integrate Firmware using test code a base to get things moving (1wk - 2wks)
- Collect power requirement data
- Evaluate performance in terms of vibration, backlash and stability
- Begin running ’wet’ runs with motorised droplet dispensing
3. Interface with electronic pipette to remotely trigger droplet dispense from controller (1wk - 2wks)
4. Running continuous testing run to optimise driving variables to minimising vibration and collect experimental data to compare to previous rigs performance (week 2 onwards)
5. Add environmental monitoring/data collection (end of prototyping, 5wks)
- Bulk of redesigning and prototyping done during this storage
- Informs the design of new parts, requirement for more components etc
6. Move electronic components ”motherboard PCB” and finalise integrated rig design and automating procedure for final deliverable(Final 4 weeks)

# Feedback

Evaluating the systems performance is now going to be two-fold. The first is as before, its performance as a new experimental rig. Does it produce more reliability and repeatability in its results, does its successfully control for the factors its has aim to control and this can be easily evaluated by comparison to the previous data collected on the old/current rig. But now I am aware the another goal of this project is the introduction of a level of automation that aim to increase the usability/flexibility of the instrumentation. What I am wondering is what would be an approach in evaluating the success of this aspect? Just that its successfully carries out a set of preprogramed motions and behaves as expects, the experiment is done etc?

# Bibliography

[1] “Stepping motors and their microprocessor controls, second edition takashi kenjo & akira sugawara, 1994 oxford, oxford university press isbn 0 19 859385 6,” European Journal of Engineering Education, vol. 20, no. 3, pp. 386–386, 1995. [Online]. Available: https://doi.org/10.1080/03043799508928291
[2] E. Gatapova, A. Semenov, D. Zaitsev, and O. Kabov, “Evaporation of a sessile water drop on a heated surface with controlled wettability,” Colloids and Surfaces A Physicochemical and Engineering Aspects, vol. 441, pp. 776–785, 01 2014.
[3] J. H. Moon, D. Kim, and S. Lee, “Spreading and receding characteristics of a nonnewtonian droplet impinging on a heated surface,” Experimental Thermal and Fluid Science, vol. 57, 09 2014.
[4] P. Hanichen, A. Bender, B. Voß, T. Gambaryan-Roisman, and P. Stephan, “Drop evap- ¨ oration of hydrocarbon fluids with deposit formation,” International Journal of Heat and Mass Transfer, vol. 128, pp. 115–124, 01 2019.
[5] M. Frasao, A. Oliveira, and R. Gonc¸alves dos Santos, “Determination of nukiyama and ˜ leidenfrost temperatures for hydrocarbons using the droplet evaporation method,” 03 2018.
[6] S. David, K. Sefiane, and L. Tadrist, “Experimental investigation of the effect of thermal properties of the substrate in the wetting and evaporation of sessile drops,” Colloids and Surfaces A: Physicochemical and Engineering Aspects, vol. 298, pp. 108–114, 04 2007.
[7] , “Implementing a step-direction interface-based stepper motor controller,” Application Note AC413, pp. 1–9, 2014.

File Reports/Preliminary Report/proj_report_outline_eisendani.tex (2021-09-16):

%% $RCSfile: proj_report_outline.tex,v $
%% $Revision: 1.3 $
%% $Date: 2016/06/10 03:41:54 $
%% $Author: kevin $

\documentclass[11pt, a4paper, oneside]{report}

\usepackage{float} % lets you have non-floating floats
\usepackage{url} % for typesetting urls
\usepackage{graphicx}
\usepackage{subcaption}
\usepackage{hyperref}
\usepackage{titlesec}
\titleformat{\chapter}[hang] 
{\normalfont\huge\bfseries}{\chaptertitlename\ \thechapter:}{1em}{} 
%
%  We don't want figures to float so we define
%
\newfloat{fig}{thp}{lof}[chapter]
\floatname{fig}{Figure}

%% These are standard LaTeX definitions for the document
%%                            
\title{Instrumentation System for Liquid Drop Impact and Evaporation}
\author{Daniel Eisen}

%% This file can be used for creating a wide range of reports
%%  across various Schools
%% 
%% Set up some things, mostly for the front page, for your specific document
%
% Current options are:
% [ecs|msor|sms]          Which school you are in.
%                         (msor option retained for reproducing old data)
% [bschonscomp|mcompsci]  Which degree you are doing
%                          You can also specify any other degree by name
%                          (see below)
% [font|image]            Use a font or an image for the VUW logo
%                          The font option will only work on ECS systems
% 
\usepackage[image,ecs]{vuwproject}

% You should specifiy your supervisor here with
\supervisor{Gideon Gouws}
% use \supervisors if there is more than one supervisor
 
\otherdegree{Bachelor of Engineering with Honours}

% Unless you've used the bschonscomp or mcompsci
%  options above use
%   \otherdegree{OTHER DEGREE OR DIPLOMA NAME}
% here to specify degree

% Comment this out if you want the date printed.
\date{}

\begin{document}

% Make the page numbering roman, until after the contents, etc.
\frontmatter
%%%%%%%%%%%%%%%%%%%%%%%%%%%%%%%%%%%%%%%%%%%%%%%%%%%%%%%
%%%%%%%%%%%%%%%%%%%%%%%%%%%%%%%%%%%%%%%%%%%%%%%%%%%%%%%

\begin{abstract}

    Droplet impact and evaporation presents a complex physical process worth investigating not only from a fundamental research perspective but also in its potential for industrial application. However, in order to extract usable data from this small scale, fast phenomenon in the lab producing a droplet of repeatable volume and position as well as accucartly track and collect the data (temperature, impact, evaporation) is essential in order to extract reliable and study worthy results. This procedure form the basis of this project.
    This projects approach is to add motorised automation to droplet dispensing with aims to control for droplet volume, positional variation, contact angle and speed up the procedure and allow for greater flexibility in the experimental process.

\end{abstract}

%%%%%%%%%%%%%%%%%%%%%%%%%%%%%%%%%%%%%%%%%%%%%%%%%%%%%%%

\maketitle

\include{acknowledge}

\tableofcontents

\mainmatter
%%%%%%%%%%%%%%%%%%%%%%%%%%%%%%%%%%%%%%%%%%%%%%%%%%%%%%%
%%%%%%%%%%%%%%%%%%%%%%%%%%%%%%%%%%%%%%%%%%%%%%%%%%%%%%%

% individual chapters included heretala
\include{introduction}
\include{background}
\include{work}
\include{future}
\include{feedback}

\backmatter
%%%%%%%%%%%%%%%%%%%%%%%%%%%%%%%%%%%%%%%%%%%%%%%%%%%%%%%
%%%%%%%%%%%%%%%%%%%%%%%%%%%%%%%%%%%%%%%%%%%%%%%%%%%%%%%

\bibliographystyle{ieeetran}
\bibliography{sample}

\end{document}

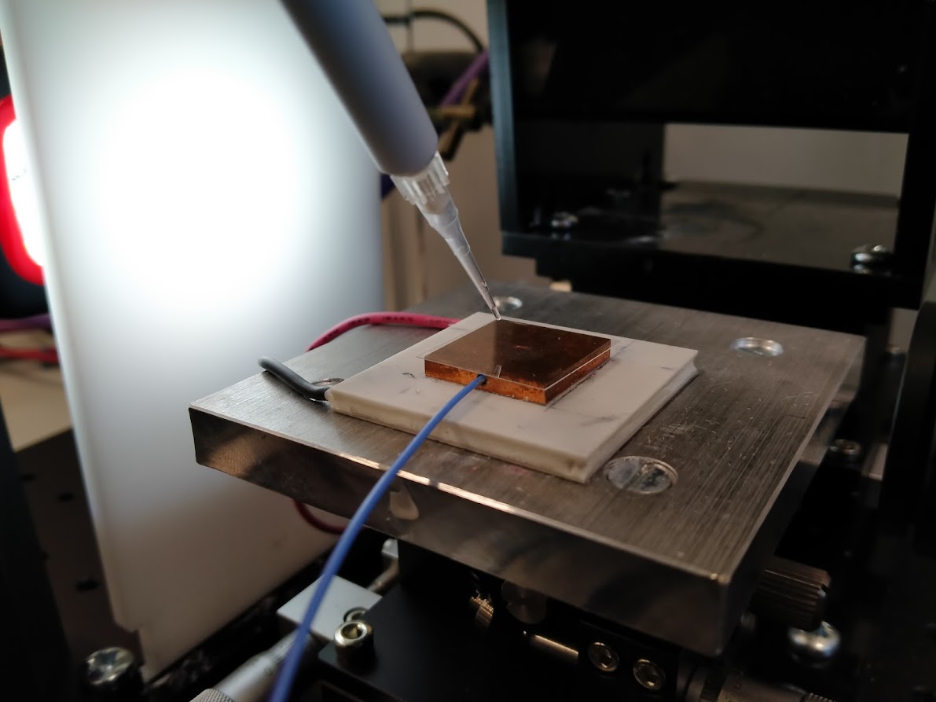
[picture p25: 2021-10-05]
Reports/Final Report/img/new_stack.jpg

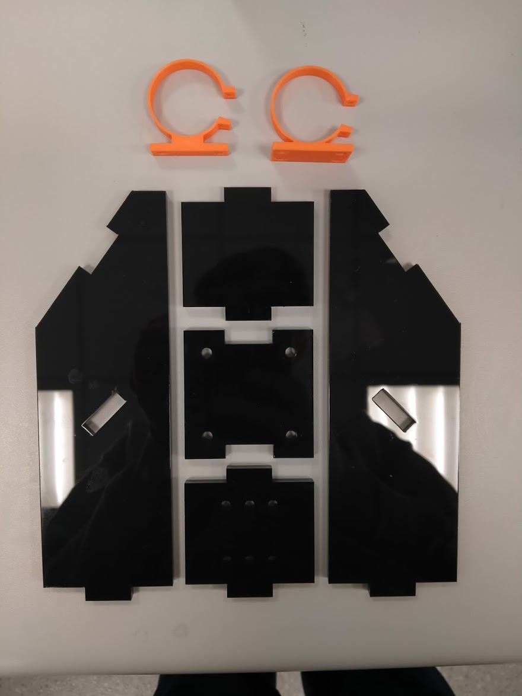
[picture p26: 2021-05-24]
Reports/Final Report/img/Tower_pcs.jpg

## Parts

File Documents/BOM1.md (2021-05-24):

| Supplier   | Stock No. | Part No.        | Qty.                       | Description                                                                | link                                                                                                                                                         |
| ---------- | --------- | --------------- | -------------------------- | -------------------------------------------------------------------------- | ------------------------------------------------------------------------------------------------------------------------------------------------------------ |
| pololu     | 2267      | SY42STH38-1684A | 2                          | NEM17 Bipolar, 200 Steps/Rev, 42×38mm, 2.8V, 1.7 A/Phase                   | https://www.pololu.com/product/2267                                                                                                                          |
| element-14 | 2507563   | ST4118M1804-A   | ***alternative to above*** |                                                                            | https://nz.element14.com/nanotec/st4118m1804-a/stepper-motor-2vdc-1-8a/dp/2507563?st=stepper                                                                 |
| pololu     | 1998      | 1998            | 1                          | Aluminum Mounting Hub for 5mm Shaft, M3 Holes (2-Pack)                     | https://www.pololu.com/product/1998/resources                                                                                                                |
| pololu     | 2133      | DRV8825         | 2                          | Stepper Motor Driver Carrier, Step/Dir, High Current, 1/32step, 1.5A/Phase | https://www.pololu.com/product/2133                                                                                                                          |
| element-14 | 143651502 | SS-3GLP BY OMZ  | 2                          | Hinge lever, limit switch/microswitch                                      | https://nz.element14.com/webapp/wcs/stores/servlet/ProductDisplay?urlLangId=64&catalogId=15001&productId=280170759&iscrfnonsku=false&langId=64&storeId=10189 |

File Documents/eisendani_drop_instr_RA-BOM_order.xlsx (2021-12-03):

Supplier | Stock No. | Part No. | Qty. | Description
pololu | 2267 | SY42STH38-1684A | 2 | NEM17 Bipolar, 200 Steps/Rev, 42×38mm, 2.8V, 1.7 A/Phase
pololu | 1998 | 1998 | 1 | Aluminum Mounting Hub for 5mm Shaft, M3 Holes (2-Pack)
element-14 | 143651502 | SS-3GLP BY OMZ | 2 | Hinge lever, limit switch/microswitch
digikey | 493-12570-1-ND | UVK1H101MPD1TD | 2 | CAP ALUM 100UF 20% 50V RADIAL

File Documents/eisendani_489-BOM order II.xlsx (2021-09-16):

Supplier | Stock No. | Part No. | Qty. | Recieved | Description
mouser | 538-35362-0250 | 35362-0250 | 8 | 0 | 2 Ckt Vert. Hdr. Sherlock W-T-B
mouser | 538-35507-0200 | 35507-0200 | 8 | 8 | 2 Ckt Housing Sherlock W-T-B
mouser | 538-35362-0450 | 35362-0450 | 4 | 4 | 4 Ckt Vert. Hdr. Sherlock W-T-B
mouser | 538-35507-0400 | 35507-0400 | 4 | 4 | 4 Ckt Housing Sherlock W-T-B
mouser | 538-50212-8100 | 50212-8100 | 32 | 50 | Headers & Wire Housings CRMP TERM 24-30G F
digikey | 1965-1000-ND | ESP32-DEVKITC-32D | 2 | 0 | WiFi Development Tools - 802.11 ESP32 General Development Kit, ESP32-WROOM-32D on the board
digikey | CP-002BH-ND | PJ-002BH | 2 | 0 | Power Barrel Connector Jack 2.50mm ID (0.098"), 5.50mm OD (0.217") Through Hole, Right Angle
digikey | 1528-4884-ND | 4884 | 1 | 0 | RP2040 Feather series ARM® Cortex®-M0+ MCU 32-Bit Embedded Evaluation Board
digikey | 2648-SC0915CT-ND | SC0915 | 1 | 1 | RP2040 Raspberry Pi Pico series ARM® Cortex®-M0+ MCU 32-Bit Embedded Evaluation Board
pololu | 2133 | DRV8825 | 2 | 0 | Stepper Motor Driver Carrier, Step/Dir, High Current, 1/32step, 1.5A/Phase
digikey | 1528-1359-ND | 2652 | 1 | 1 | BME280 series Humidity, Pressure, Temperature Sensor Evaluation Board
digikey | 1528-4650-ND | 4650 | 1 | 1 | OLED 1.3" Display Feather Platform Evaluation Expansion Board
adafruit | 4237 | LIPO 552530 | 1 | 1 | Lithium Ion Polymer Battery with Short Cable - 3.7V 350mAh

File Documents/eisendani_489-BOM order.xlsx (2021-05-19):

Supplier | Stock No. | Part No. | Qty. | Description
pololu | 2267 | SY42STH38-1684A | 2 | NEM17 Bipolar, 200 Steps/Rev, 42×38mm, 2.8V, 1.7 A/Phase
element-14 | 2507563 | ST4118M1804-A | ***alternative to above***
pololu | 1998 | 1998 | 1 | Aluminum Mounting Hub for 5mm Shaft, M3 Holes (2-Pack)
pololu | 2133 | DRV8825 | 2 | Stepper Motor Driver Carrier, Step/Dir, High Current, 1/32step, 1.5A/Phase
element-14 | 143651502 | SS-3GLP BY OMZ | 2 | Hinge lever, limit switch/microswitch

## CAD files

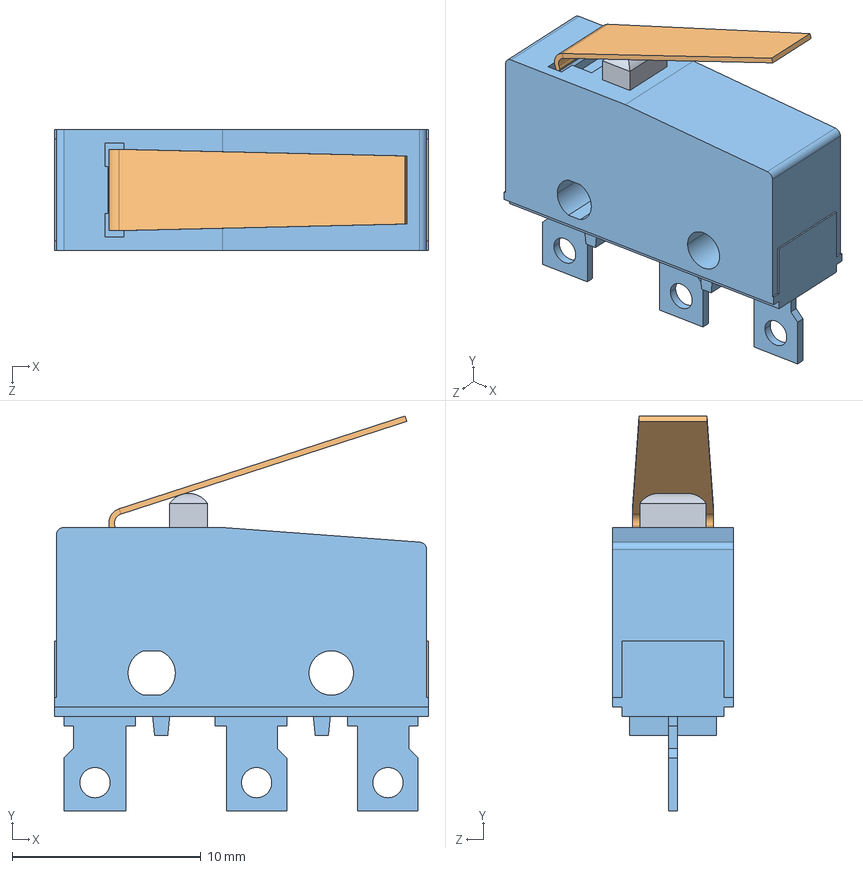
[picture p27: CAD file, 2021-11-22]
Documents/CAD/SS_3GLP.step
19.8 x 20.9 x 6.40 mm
SS_3GLP_ACTUATOR2
SS_3GLP_ACTUATOR1
SS_3GLP_BASE

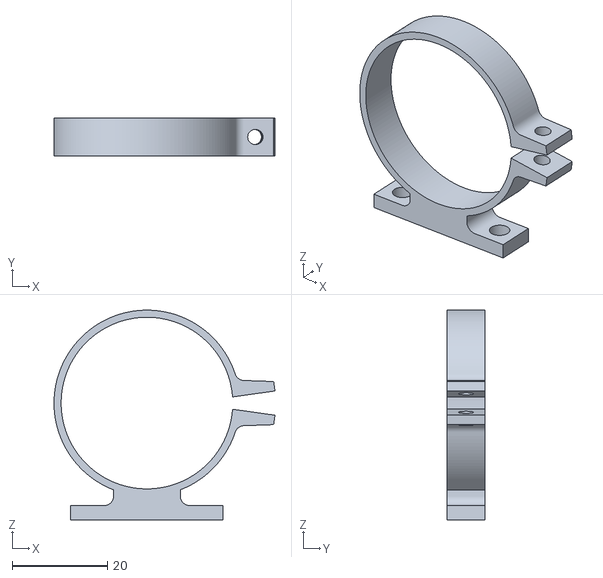
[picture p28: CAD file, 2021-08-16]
Documents/CAD/ring_clamp_b_36_rev2.stl
46.4 x 8.00 x 44.0

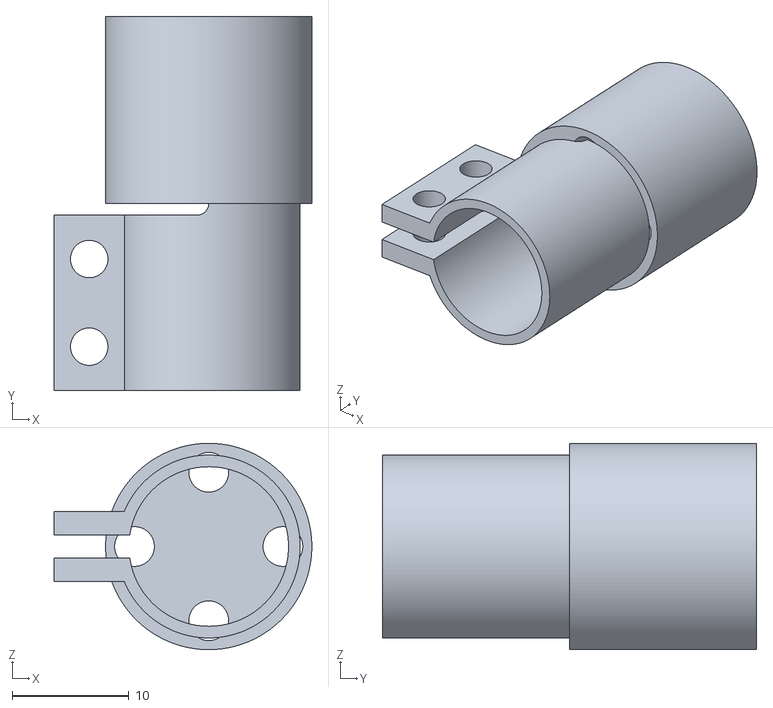
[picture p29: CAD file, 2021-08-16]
Documents/CAD/Z_umeter_coupler - slide_coupler_rev2.stl
22.1 x 32.0 x 17.7

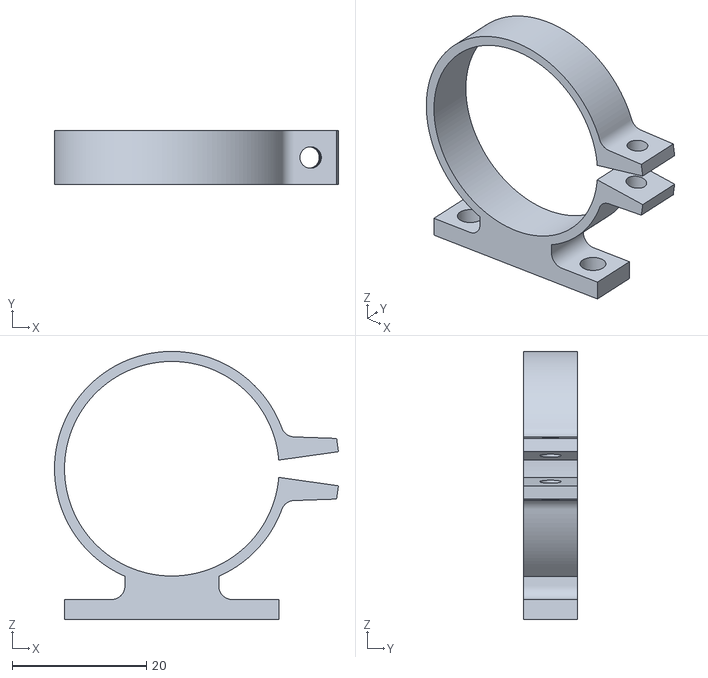
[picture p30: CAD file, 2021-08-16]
Documents/CAD/ring_clamp_a_32_rev2.stl
42.4 x 8.00 x 40.0

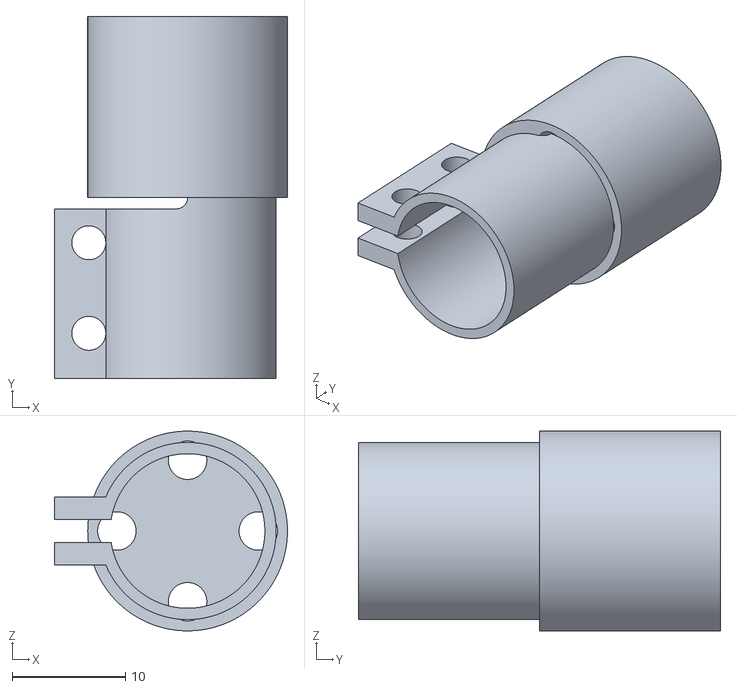
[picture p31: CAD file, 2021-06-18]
Documents/CAD/Z_umeter_coupler - slide_coupler.stl
20.6 x 32.0 x 17.7

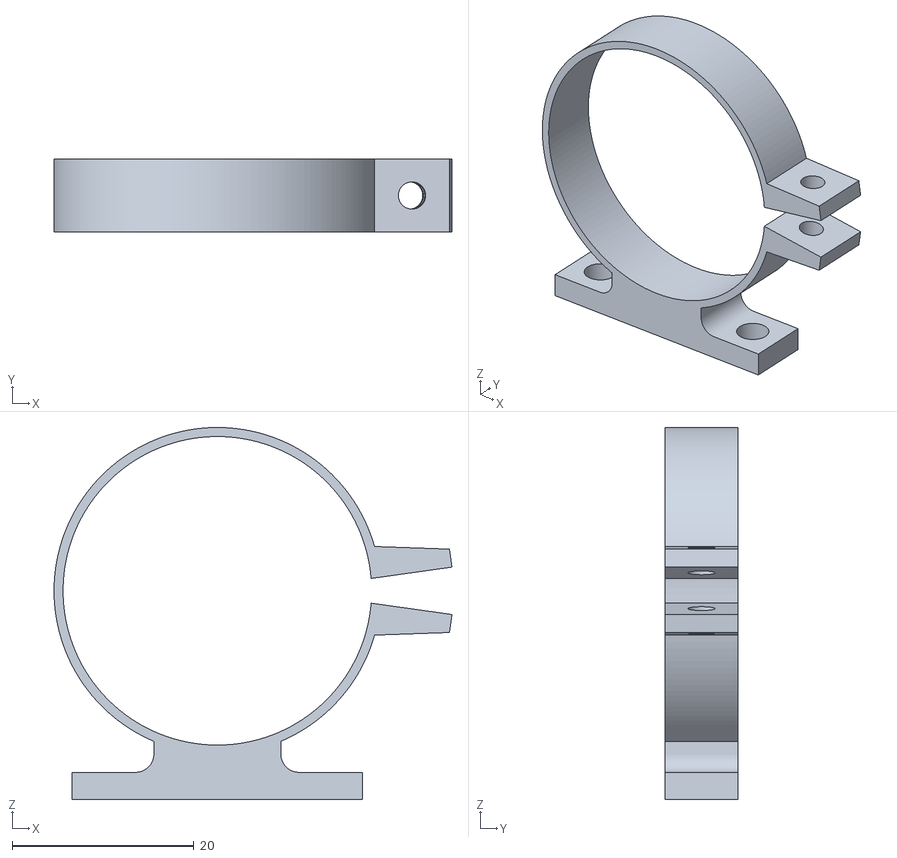
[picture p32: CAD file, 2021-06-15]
Documents/CAD/ring_clamp_b_36.stl
43.9 x 8.00 x 41.0

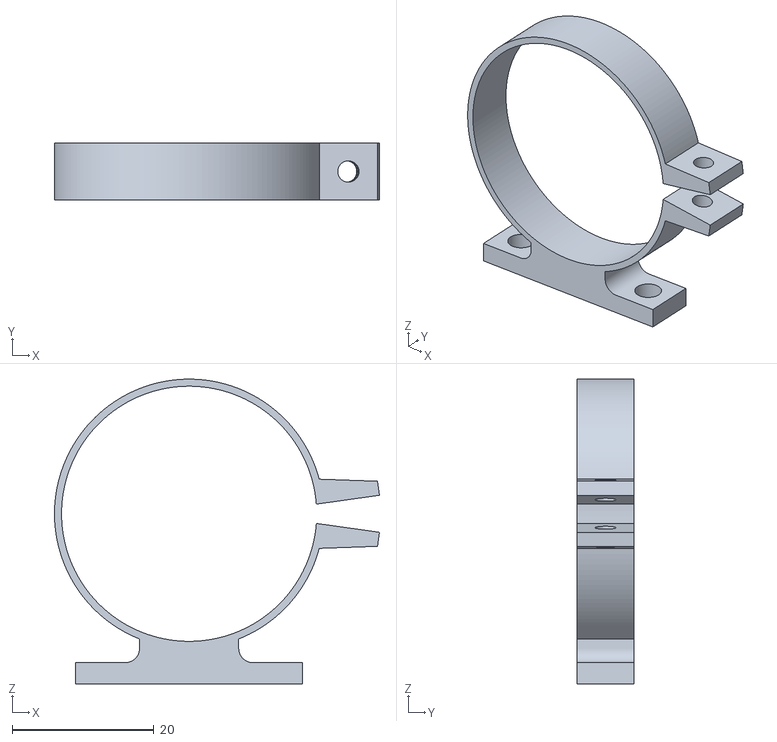
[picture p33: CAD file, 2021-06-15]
Documents/CAD/ring_clamp_b_38.stl
45.9 x 8.00 x 43.0

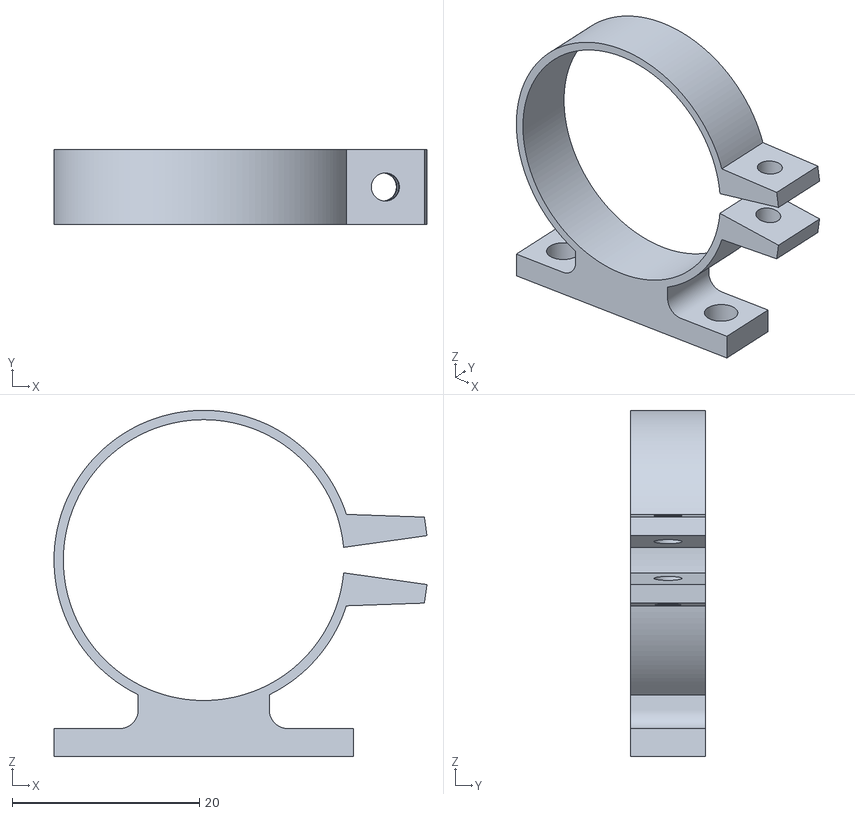
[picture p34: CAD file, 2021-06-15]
Documents/CAD/ring_clamp_a_32.stl
39.9 x 8.00 x 37.0

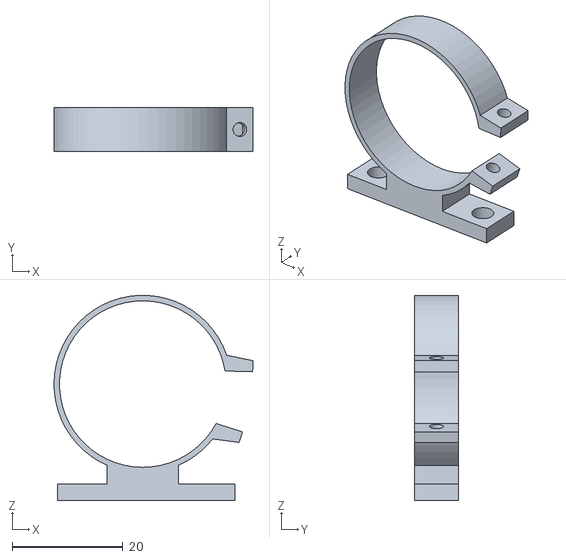
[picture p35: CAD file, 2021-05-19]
Documents/CAD/Part Studio 1 - ring_clamp_5mm.stl
35.9 x 8.00 x 37.0

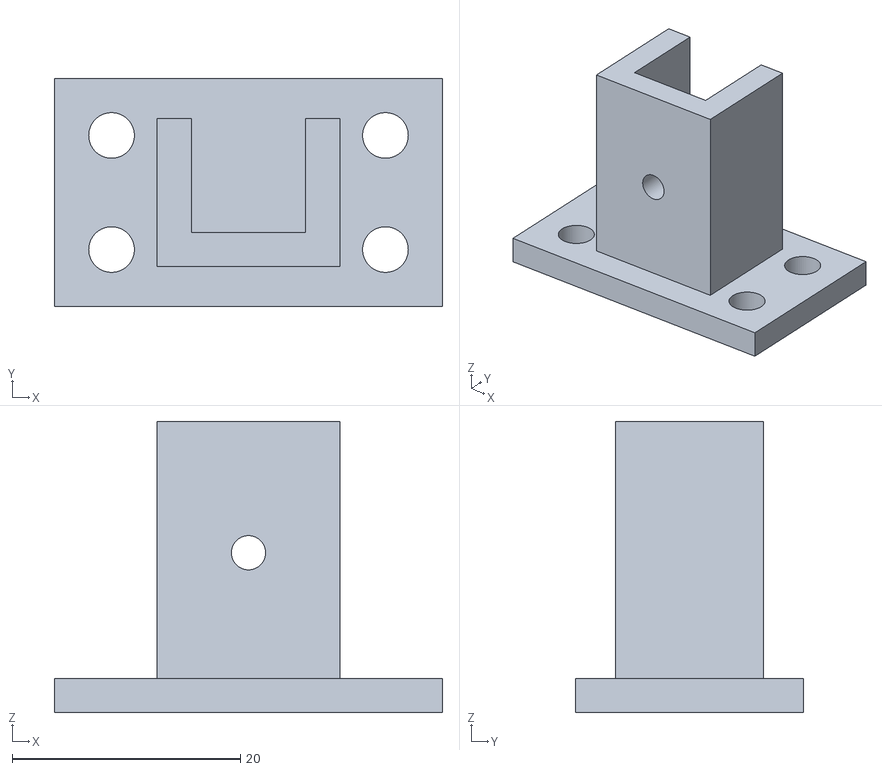
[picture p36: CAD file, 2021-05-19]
Documents/CAD/Part Studio 1 - mount_adapt.stl
34.0 x 20.0 x 25.5

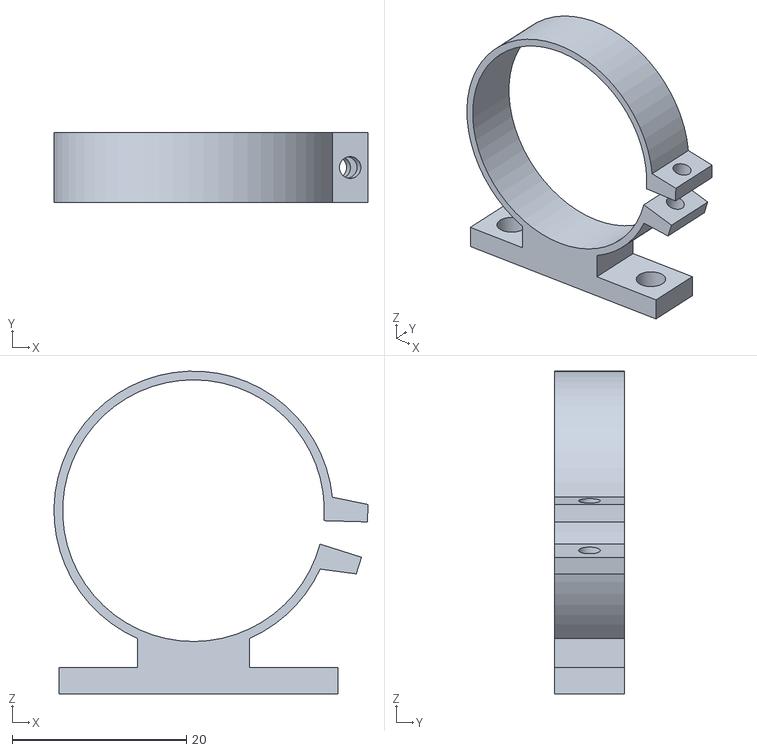
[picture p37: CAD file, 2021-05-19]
Documents/CAD/Part Studio 1 - ring_clamp.stl
36.0 x 8.00 x 37.0

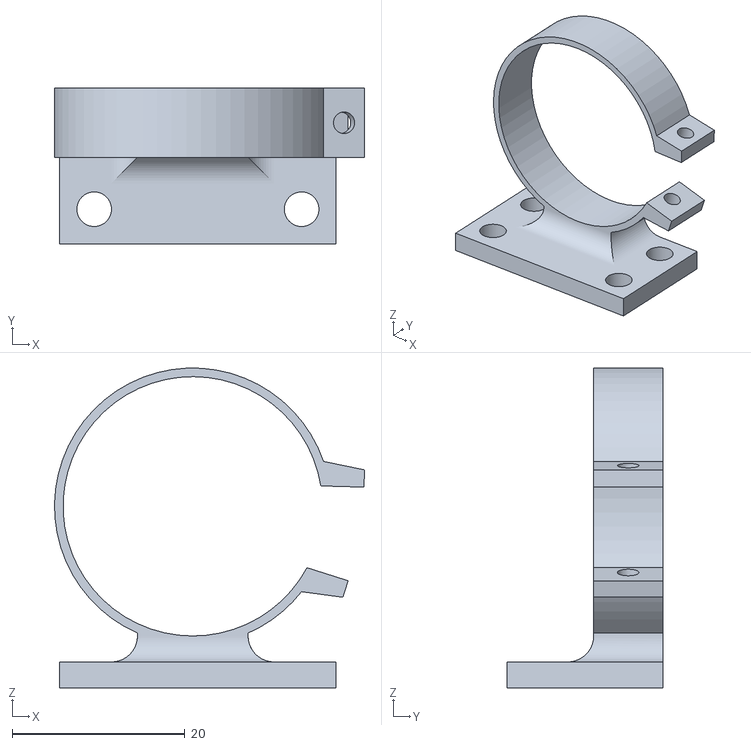
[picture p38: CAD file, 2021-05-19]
Documents/CAD/Part Studio 1 - ring_clamp_wide.stl
35.9 x 18.0 x 37.0

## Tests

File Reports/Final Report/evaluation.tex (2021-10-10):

\chapter{Evaluation}\label{C:eval}

The aim of this project was to control for and improve the repeatability, and reliability of the position and volume of the dispensed droplets on a substrate with the informed hypothesis that these are major contributors to the observed high variation in resulting the temperature evolution during the droplet's evaporation. To show the success of the project this evaluation will investigating, quantify and compare the performance and positional repeatability of the new instrumentation as well begin to as investigate its effects on the temperature evolution of the droplet's evaporation.

\section{Mechanical Stability}

Given that the express goal of this project is to produce a more stable, repeatable system for depositing droplets of a set position the mechanical stability of the instrumentation is required to be accessed and tuned to minimise vibration and pipette tip oscillations (settling time and overshoot).

To evaluate the performance of the system, a parameter sweep of the pipettes R stage motor driving settings: speed and ramp acceleration.
\subsection{Procedure}
\begin{itemize}
    \item Position tip at -1/4 revolution before zero point (proxy reservoir)
    \item Set Speed/acceleration values
    \item Swing to zero position
    \item Repeat for values across sweep: speed=1rev/s, acc=1/rev/s/s $\rightarrow$  speed=2rev/s, acc=10/rev/s/s
    \item Note: acceleration is the ramp down at end/start of motion so is what we care most about
\end{itemize}

\subsection{Results}
By taking a 25 frames per second image sequence captured via the top camera of the same automated sequence performed at various parameters the pipette tip could be motion-tracked over time to extract its relative motion frame to frame quantitatively capture the settling behaviour of the pipette tip. Minimising ensured the best chance of avoiding prematurely detachment and precise positioning at the time of dispense. 

\begin{figure}[h]
    \centering
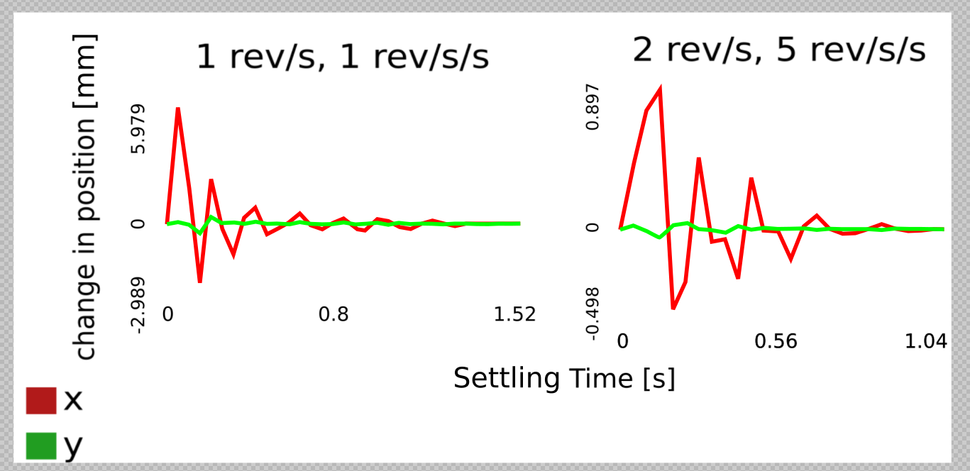
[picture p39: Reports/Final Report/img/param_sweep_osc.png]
    
    \caption{Worst (Left) and Best (Right) performing oscillations and settings}
    \label{Fig:tip_osc}
\end{figure}

The figure [\ref{Fig:tip_osc}] above shows this tip behaviour. This procedure and analysis helped determine a final parameter tuning for the R motor of 2 rev/s and 5 rev/s/s resulting in a maximum overshoot of 0.9mm and settling time of 1s. This can be used to inform the delay time require after tip positioning before dispensing the droplet.

\section{Droplet Volume}

Something the previous system could not achieve was accurately dispensing a variety of volumes.

\begin{wrapfigure}{r}{0.33\textwidth}
    \centering
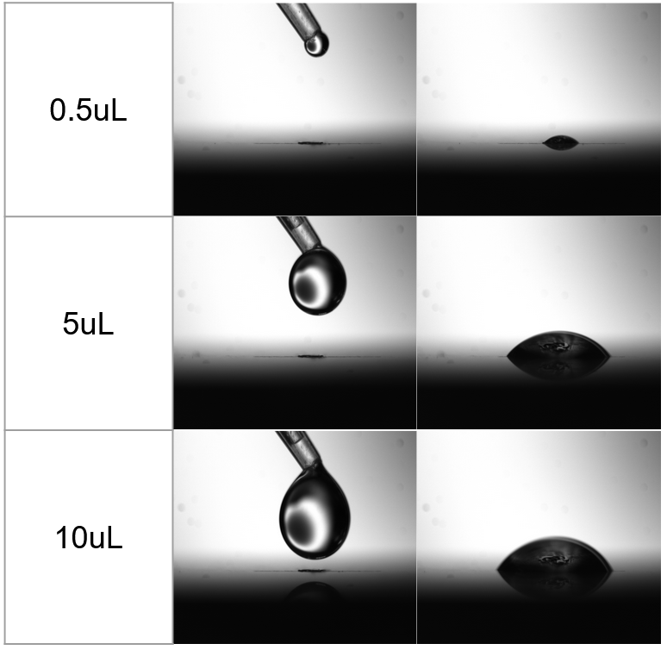
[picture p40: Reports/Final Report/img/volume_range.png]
    
    \caption{Successful droplet dispense and deposit of full volume range}
    \label{fig:vol_var}
\end{wrapfigure}

The use of an e-pipette eliminates variation in absolute volume to a higher precision than what this project can evaluate but additionally the use of it programmable volume feature enables this. The instrumentation however may not be able to use the full volume range of $0.5\mu L$ to $10\mu L$.

The system had been observed previously to be unable to reliably dispense above $8\mu L$ without premature detachment. This was before the Z motor coupler was refined and the motors speed adjusted.
We also had the hypothesis that variation in volume could have an effect on the y-position of the deposited droplet, via the mechanism of differing masses being affected more by surface tension with the tip.

The figure \ref{fig:vol_var}shows instrumentation successfully dispensing and depositing the full range of volumes, and confirms the systems ability to utilise the pipettes full functionality. Also of note that these results disprove the hypothesis of y-axis dependency, as after dispensing [if a delay of at least 500ms is allowed] all droplet volumes hang and settle with gravity.  

To ensure consistent performance over the volume range the Z-height dip must be varied to successfully deposit the droplet on the substrate and prevent overly deforming it at high volume.

\begin{figure}[h]
    \centering
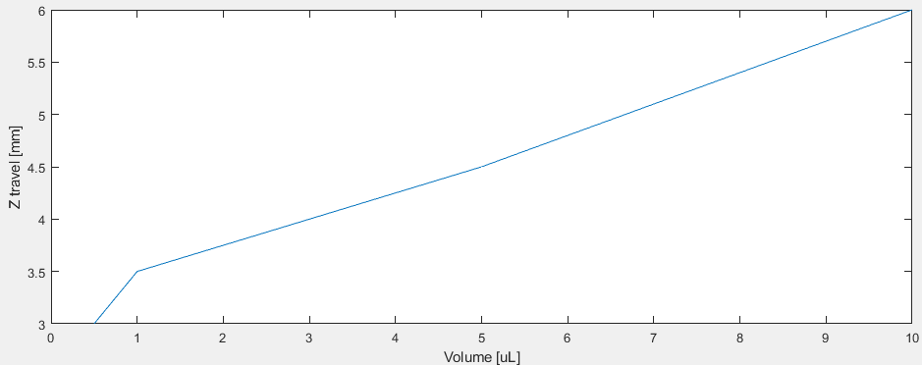
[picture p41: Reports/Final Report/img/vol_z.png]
    
    \caption{Drop Volume vs Required Z travel}
\end{figure}

\section{Repeatability and Reliability}

This section aims to produce the main set of comparable results for evaluating the projects produced system against the output of the previous setup. Thus justifying the success of one of main goals.

\subsection{Procedure}
\begin{itemize}
    \item \textbf{Initial Setup:} Roughly Position substrate stage, reservoir platform and note angular positions as well as vertical clearance requirements.
    \item \textbf{Zero System:} Using overhead camera precisely position pipette tip above substrate centre
    \item \textbf{Data Acquisition:} Initialise cameras, collect pixel:mm calibration data for analysis, initial LabView temperature logger, and environmental monitor noted. Info: temperature data rate, camera frame rate
    \item \textbf{Automated Sequence:} Via the serial link, enter the procedures command sequence to represent $\rightarrow$ lower, draw up fluid, raise, position over the substrate, dispense, lower, raise, clear camera view. With appropriate delays.
    \item \textbf{Capture:} Begin data collection and automated dispense.
    \item \textbf{Repeat: } 3 times. Each time carefully cleaning substrate surface to minimised up measured factors.
\end{itemize}

\subsection{Analysis and Results}
To show the system successfully increases the consistency of droplet position and investigate whether this supports the hypothesis that this resulted in better temperature consistency.

\subsection{Position}

The main bulk of the design and effort of this project were put towards ensuring consistent, accurate and repeatable pipette tip positioning with the intention of greatly decrease the run to run variance in droplet position. This was due to the static point temperature measurement being taken by a thermocouple and initial evaluation indicating a correlation between droplet offset from thermocouple position and temperature data variation.

\begin{figure}[h]
    \centering
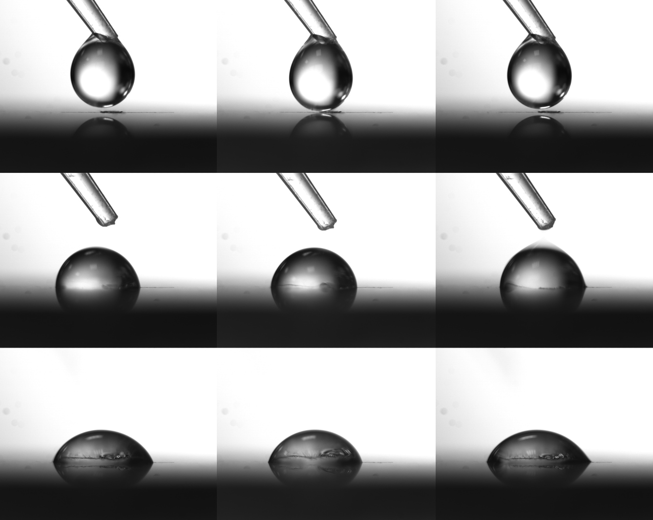
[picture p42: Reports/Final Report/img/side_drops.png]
    
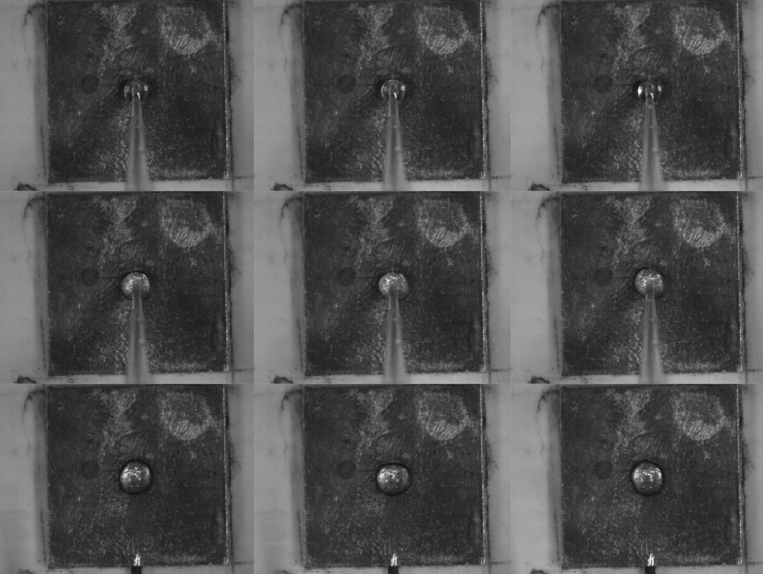
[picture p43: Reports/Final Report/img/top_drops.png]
    
    \caption{Visual results of consecutive experimental runs (Runs are column-wise)}
    \label{fig:drops_eval}
\end{figure}

Prior sections have covered to tuning and design decisions taken to produce consist pipette tip position but how does this translate to droplet variation. Figure  \ref{fig:drops_eval}shows the qualitative results of 3 consecutive 10 $\mu L$ experiments. By observing these results, the pipette tip placement is indistinguishable between runs and hanging droplets before contact are also consistent. This image data formed the basis for further analysis to extract quantitative information.

Collected calibration reference images allows the translation of pixels to mm, and using an image processing and analysis tool droplet centre offset from substrate centre as well as surface contact area measured to quantify performance for comparison to initial system.

\begin{figure}[h]
    \centering
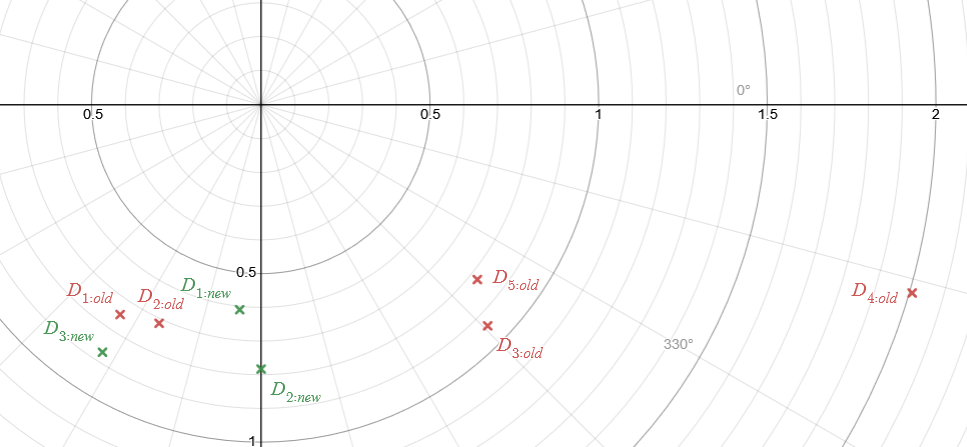
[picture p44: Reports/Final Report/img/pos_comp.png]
    
    \caption{Caparison of old (red) and new (green) droplet positions}
\end{figure}

\subsection{Temperature Evolution}

The above droplet runs were also accompanied by the collection of substrate temperature data via the embedded thermocouple. The thermocouple was read at 30Hz, and MatLab was used to postprocess and analyse the data. As a pre-processing step a 1sec rolling average is applied to the collected vectors. They are then time aligned to zero at the point of droplet contact, indicated by sudden temperature drop. This The data is then transformed into a temperature delta relative to the temperature just before contact. 

\begin{figure}[h]
    \centering
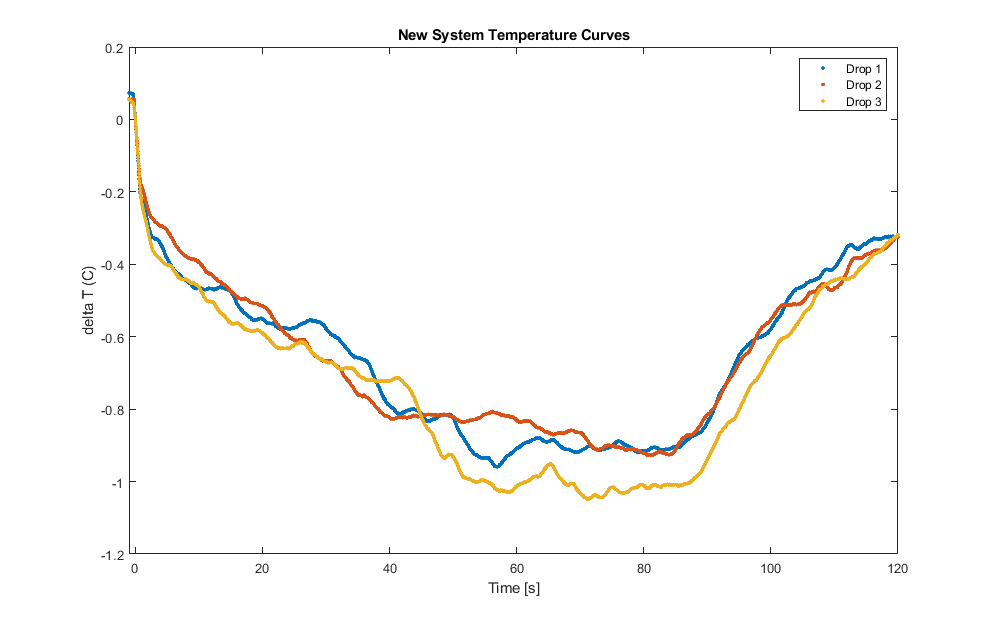
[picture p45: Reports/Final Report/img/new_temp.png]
    
    \caption{Captured Temperature Evolution of new drop tests}
\end{figure}

It is worth noting that this temperature data is in no way comprehensive, and differs from the initial data due to a difference in substrate material: stainless steel vs copper. 

\subsection{Summery}

\begin{table}[h]
    \centering
    \begin{tabular}{|l|l|l|l|}
    \hline
             & Pos Offset {[}mm{]} & delta T {[}c{]} & contact area ($mm^2$)  \\ \hline
    Drop 1   & 0.6126              & -0.9044         & 15.8928                               \\ \hline
    Drop 2   & 0.7856              & -0.9238         & 15.7082                               \\ \hline
    Drop 3   & 0.8728              & -1.009          & 15.0274                               \\ \hline
    Variance & 0.01753948          & 0.003096        & 0.20774716   \\ \hline
    \end{tabular}
    \end{table}

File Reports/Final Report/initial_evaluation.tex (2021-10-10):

\chapter{Initial Evaluation}\label{C:init_eval}

\section{Initial Experimental Setup at Project Start}
Given that the express purpose of the project is the development of a new version of instrumentation, the first step is an examination of the prior system. This is to identify how it falls short and to determine the areas that the project will focus on.

The experimental method concerns depositing a liquid droplet upon a heated substrate. The data of note is the temperature evolution of the substrate directly under the drop, as well as image data capturing the point of impact and how the droplet changes over the course of the evaporation.

\vspace*{-16pt}
\begin{figure}[h]
    \begin{center}
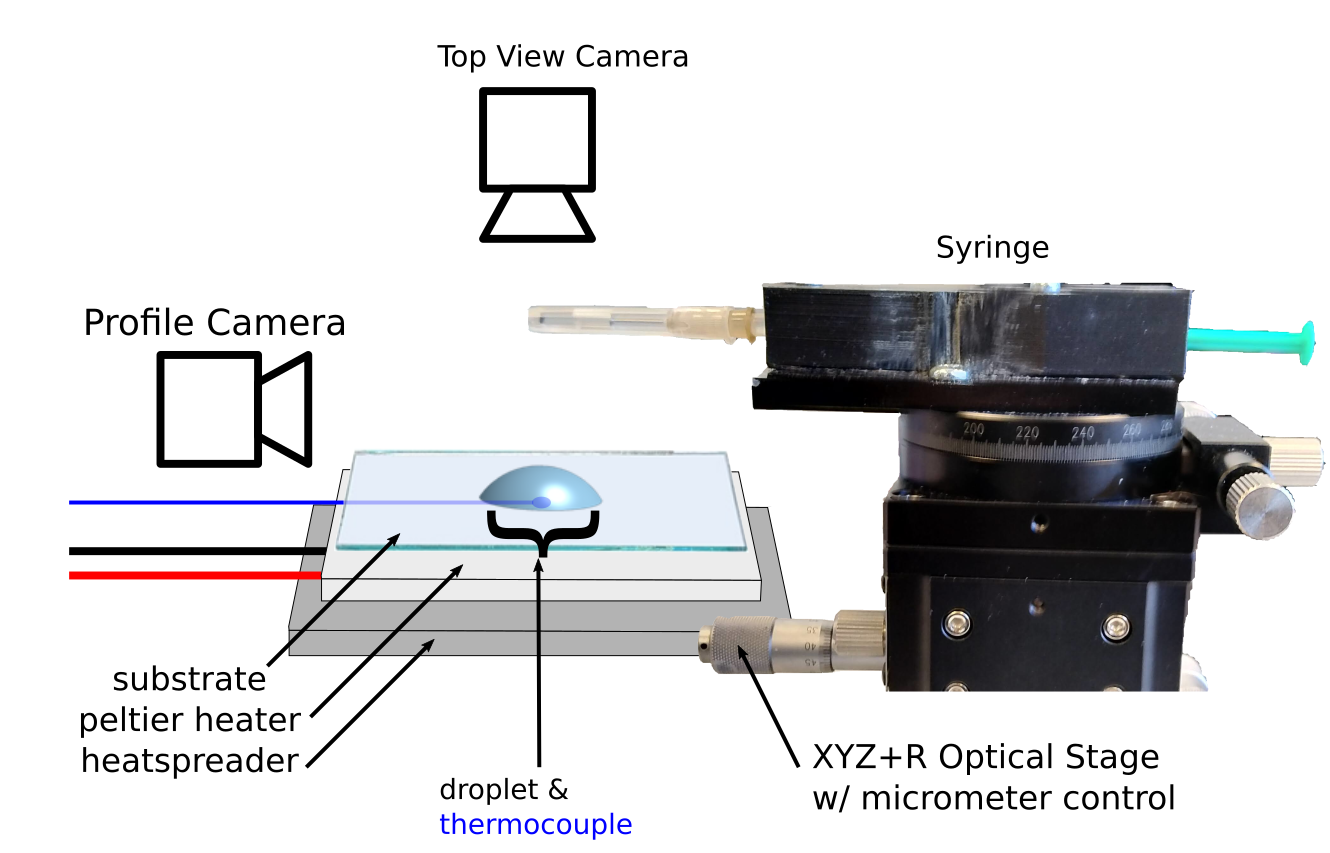
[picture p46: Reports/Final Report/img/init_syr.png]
        
        \caption{Initial Experimental Setup}
        \label{fig:prior_exp}
    \end{center}
\end{figure}
\vspace*{-16pt}

The prior system uses an optical breadboard and micrometer adjustable stages as mounting platforms and positional control.
A central stage holds the substrate stack, consisting of an aluminium heat-spreader, Peltier heater, and metallic substrate (copper, stainless steel, etc) with an internally mounted thermocouple.
To capture the image data, a pair of manual focus cameras are positioned/suspended in profile and top-down view and are controlled via a USB connection. The thermocouple is sampled with LabVIEW via a USB DaQ.
Dispensing the droplet itself is done by hand using a syringe mounted to another optical stage [\ref{fig:prior_exp}] with XYZ+R controls. It is rotated above the substrate and pressed to dispense a drop.

This would be perfectly fine, however, the results this manual process yields had a level of inconsistency. Thus motivating the design of a new system to control for the experiments variation.

\section{Repeatability and Reliability}
To identify more precisely the drawbacks in the performance of the prior setup and inform the requirements of the project, previously collected data was first analysed.

The data was taken from a series of five droplet runs, and was analysed to quantify the repeatability and reliability of the system and to compare the effect of the drop morphology and position with the resulting temperature evolution.

\begin{figure}[h]
    \centering
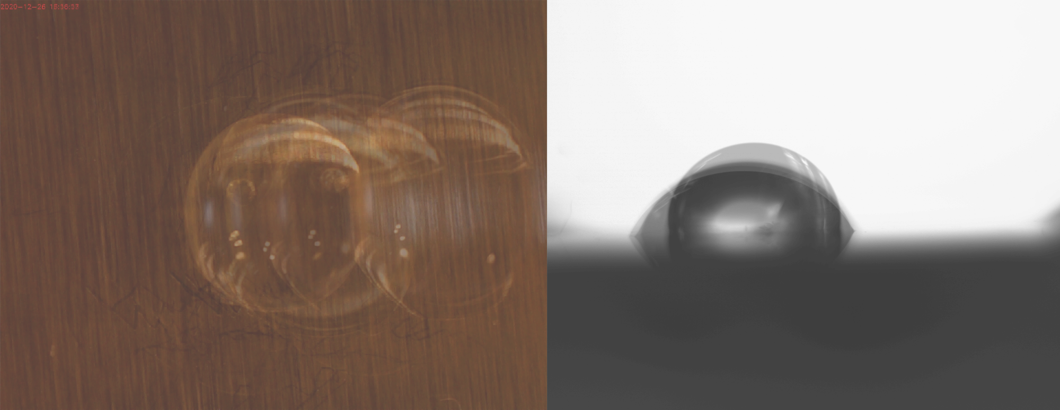
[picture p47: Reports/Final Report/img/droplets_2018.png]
    
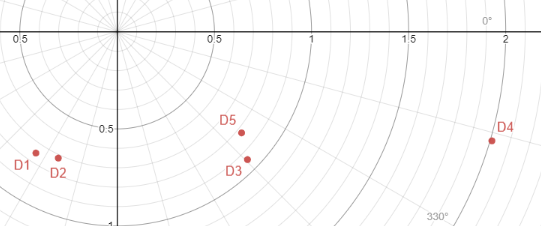
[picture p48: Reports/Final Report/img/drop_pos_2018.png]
    
    \caption{Droplet positional and shape variation; Left: Camera overlay, Right: Quantified Offsets [mm $\angle$ degrees]}
    \label{fig:init_pos}
\end{figure}

The first analysis is the image data. The substrate itself has a mark to represent the position of the thermocouple, this is used as the main reference to quantify the droplet position. Reference images set calibration at 120.14 pixels/mm and 109.2 pixels/mm for the top down and profile cameras respectively, and was used to measure the droplet centre offset and angle (from the reference point) as well as the height, width and contact angles of the droplet on the substrate.

As seen above, the quite substantial positional variation between the runs. Ranging [0.71:2.01]mm offset and [-16:-123]$^\circ$ angle.

\begin{equation}
    \frac{1}{6}\pi h(3a^2 + h^2)
    : a \equiv \mathrm{half \; width}, \; h \equiv \mathrm{height}
    \label{equ:vol}
\end{equation}
From the data extracted from the profile camera (height, width, contact angle) the volume of the droplets could be estimated. The method chosen was of the represent the droplet as a spherical cap and use the above equation \ref{equ:vol}to compute it.

\begin{figure}[h]
    \centering
    
    
    \caption{Left: Initial Systems temperature data showing large relative variation, Right: Drop offset magnitude (mm) against resulting measured temperature drop}
\end{figure}

By taking a series of consecutively collected temperature data using the initial system the observed variation can be quantified. As a pre-processing step a 1sec rolling average is applied to the collected vectors. They are then time aligned to zero at the point of droplet contact, indicated by a sudden temperature drop. This data is then transformed into a temperature delta relative to the temperature just before contact. 

Observed is $0.112^\circ C$ variance between the initial temperature drops between all runs and all runs are observed to evolve at differing rates, rebounding to drifting temperatures etc. This is the main justifying factor in perusing an improved instrumentation system.   

\newpage
\section{Summary}

\begin{table}[h]
    \centering
    \begin{tabular}{|l|l|l|l|}
        \hline
        \textit{\textbf{Droplet}}                          & \textit{Offset(mm)} & \textit{Volume(uL)} & \textit{delta T (c)}\\ \hline
        \cellcolor[HTML]{9698ED}1                          & 0.7506              & 16.55               &  -1.649861        \\ \hline
        \cellcolor[HTML]{E9AD3F}2                          & 0.7164              & 17.91               &  -1.790142        \\ \hline
        \cellcolor[HTML]{C0C0C0}3                          & 0.9402              & 17.89               &  -1.294989        \\ \hline
        \cellcolor[HTML]{FFFC9E}4                          & 2.0104              & 17.57               &  -0.994441        \\ \hline
        \cellcolor[HTML]{79CD5D}5                          & 0.8258              & 16.21               &  -1.712207        \\ \hline
        \cellcolor[HTML]{FFFFFF}\textbf{\textit{Variance}} & \textit{0.2964}     & \textit{0.6288}     &  \textit{0.1121527 }       \\ \hline
    \end{tabular}
\end{table}

To summarise the results of this initial evaluation, a variance of the droplets morphology and resulting temperature measurement are taken and used as a guide for the projects specification and comparative evaluation.    

To fully guide and justify the direction this project will take in attempting to improve this experiment it will consider and address a list of possible affecters on the experiment results.

\begin{table}[h]
    \centering
    \begin{tabular}{|l|l|l|}
        \hline
        \textbf{Effector} & \textbf{Likelihood} & \textbf{Effect Strength} \\ \hline
        Position          & HIGH                & HIGH                     \\ \hline
        Volume            & MODERATE            & HIGH                     \\ \hline
        Contact angle*    & MODERATE            & MODERATE                     \\ \hline
        Humidity          & LOW                 & HIGH                     \\ \hline
        Temperature       & LOW                 & HIGH                     \\ \hline
        Pressure          & MODERATE            & MODERATE                 \\ \hline
    \end{tabular}
\end{table}
\textit{\small{*Contact angle is more a function of the surface cleaning of the substrate, and is only representative of the surface area of contact with the substrate}} \\

Droplet position is a result of the method of dispensing and as seen in figure 3.3 correlates to variation in the observed temperature data collected via the substrates embedded thermocouple. Due to the manual method of dispensing, this variation is very likely to occur and is essentially uncontrolled in the initial experiment other than a reference point as a target. 
The volume and Contact angle of the droplet is more a result of procedural inconsistencies. The volume being a factor of the syringe and contact angle being very dependant of the surface finish/quality/cleaning of the substrate.

The environmental factors differ from these, as the experiment is carried out in a climate-controlled lab there are very few high-frequency changes but these factors can greatly affect the rate of evaporation of the droplet.

Given the above, this project will focus on the controlling the procedural affecters but will supply a method for collecting data on the environmental affecters for analysis.

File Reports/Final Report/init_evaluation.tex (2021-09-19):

\chapter{Initial Evaluation}\label{C:init_eval}

\section{Current Experimental Setup}
The instrumentation as exists is assembled with an optical breadboard and XYZ+R stages with micrometre controls. A central stage holds the substrate with internally mounted thermocouple. Two manual focus cameras are positioned in profile and top down views, and the droplet is dispensed manually via a syringe mounted horizontally to a XYZ+R stage.
The current procedure is a manual process. The syringe tip is rotated above a marked point on the substrate, and hand emptied and refilled. This results in volume and positional variation between runs. This procedural variance is the focus of this project.

\section{Repeatability and Reliability}

Data taken from a series of five droplet runs was analysed to extract the variety in droplets and its effect on the measure temperature profile. 

\begin{figure}[h]
    \begin{center}
        
        

        
        
    \end{center}
\end{figure}

\begin{table}[h]
    \centering
    \begin{tabular}{|l|l|l|}
    \hline
    \textit{\textbf{Droplet}} & \textit{Distance from Centre (mm)} & \textit{Estimated Volume (mm\textasciicircum{}2)} \\ \hline
    \cellcolor[HTML]{9698ED}1 & 0.7506                             & 16.55                                             \\ \hline
    \cellcolor[HTML]{E9AD3F}2 & 0.7164                             & 17.91                                             \\ \hline
    \cellcolor[HTML]{C0C0C0}3 & 0.9402                             & 17.89                                             \\ \hline
    \cellcolor[HTML]{FFFC9E}4 & 2.0104                             & 17.57                                             \\ \hline
    \cellcolor[HTML]{79CD5D}5 & 0.8258                             & 16.21                                             \\ \hline
    \end{tabular}
    \end{table}

\begin{table}[h]
    \centering
    \begin{tabular}{|l|l|l|}
    \hline
                   & \textit{Distance from Mark}          & \textit{Measured Temperature Drop} \\ \hline
    Min Pos Offset & 0.71mm                     &-1.7901$^{\circ}C$    \\ \hline
    Max Pos Offset &       2.01mm    &  -0.9944$^{\circ}C$    \\ \hline
                   & \textit{Volume}            & \textit{Contact Angle}          \\ \hline
    Shape Variance & $0.629mm^3$ & 25.894 degrees $\dagger$                \\ \hline
    \end{tabular}
    \caption{Variance in Setup}
    \subcaption*{$\dagger$This excluded an outlier of an almost spherical droplet with contact angles exceeding 95 degrees. This large variation is most likely due to inconsistency in surface chemisty from washing.}
    \end{table}

\section{Revised Approach}
The focus of the project is now twofold. Firstly on the automation of the process to allow for faster, pre-programmed runs to be carried out easier, and secondly to improve on the repeatability and reliability of the results by controlling the procedural factors of the experiment. 

\begin{table}[]
    \begin{tabular}{lll}
    \textbf{Affector} & \textbf{Liklihood} & \textbf{Effect Strength} \\
    Position          &                    &                          \\
    Volume            &                    &                          \\
    Contact angle*    &                    &                          \\
    Humidity          &                    &                          \\
    Temperature       &                    &                          \\
    Pressure          &                    &                         
    \end{tabular}
    \end{table}

An electronic pipette will be used to dispense a precise volume, and motorised stages will be used to provide preprogrammed, repeatable motion. The environmental factors however are not to be ignored, though controlling them is outside of the scope of this project. They will, however, be monitored, and this project will implement data collection of temperature, atmospheric pressure and humidity so these factors can be correlated to any remaining variation in data.

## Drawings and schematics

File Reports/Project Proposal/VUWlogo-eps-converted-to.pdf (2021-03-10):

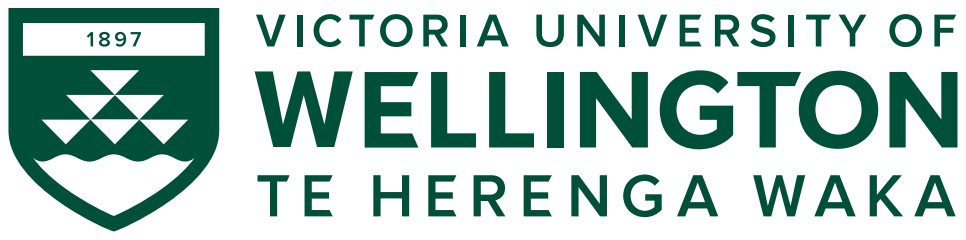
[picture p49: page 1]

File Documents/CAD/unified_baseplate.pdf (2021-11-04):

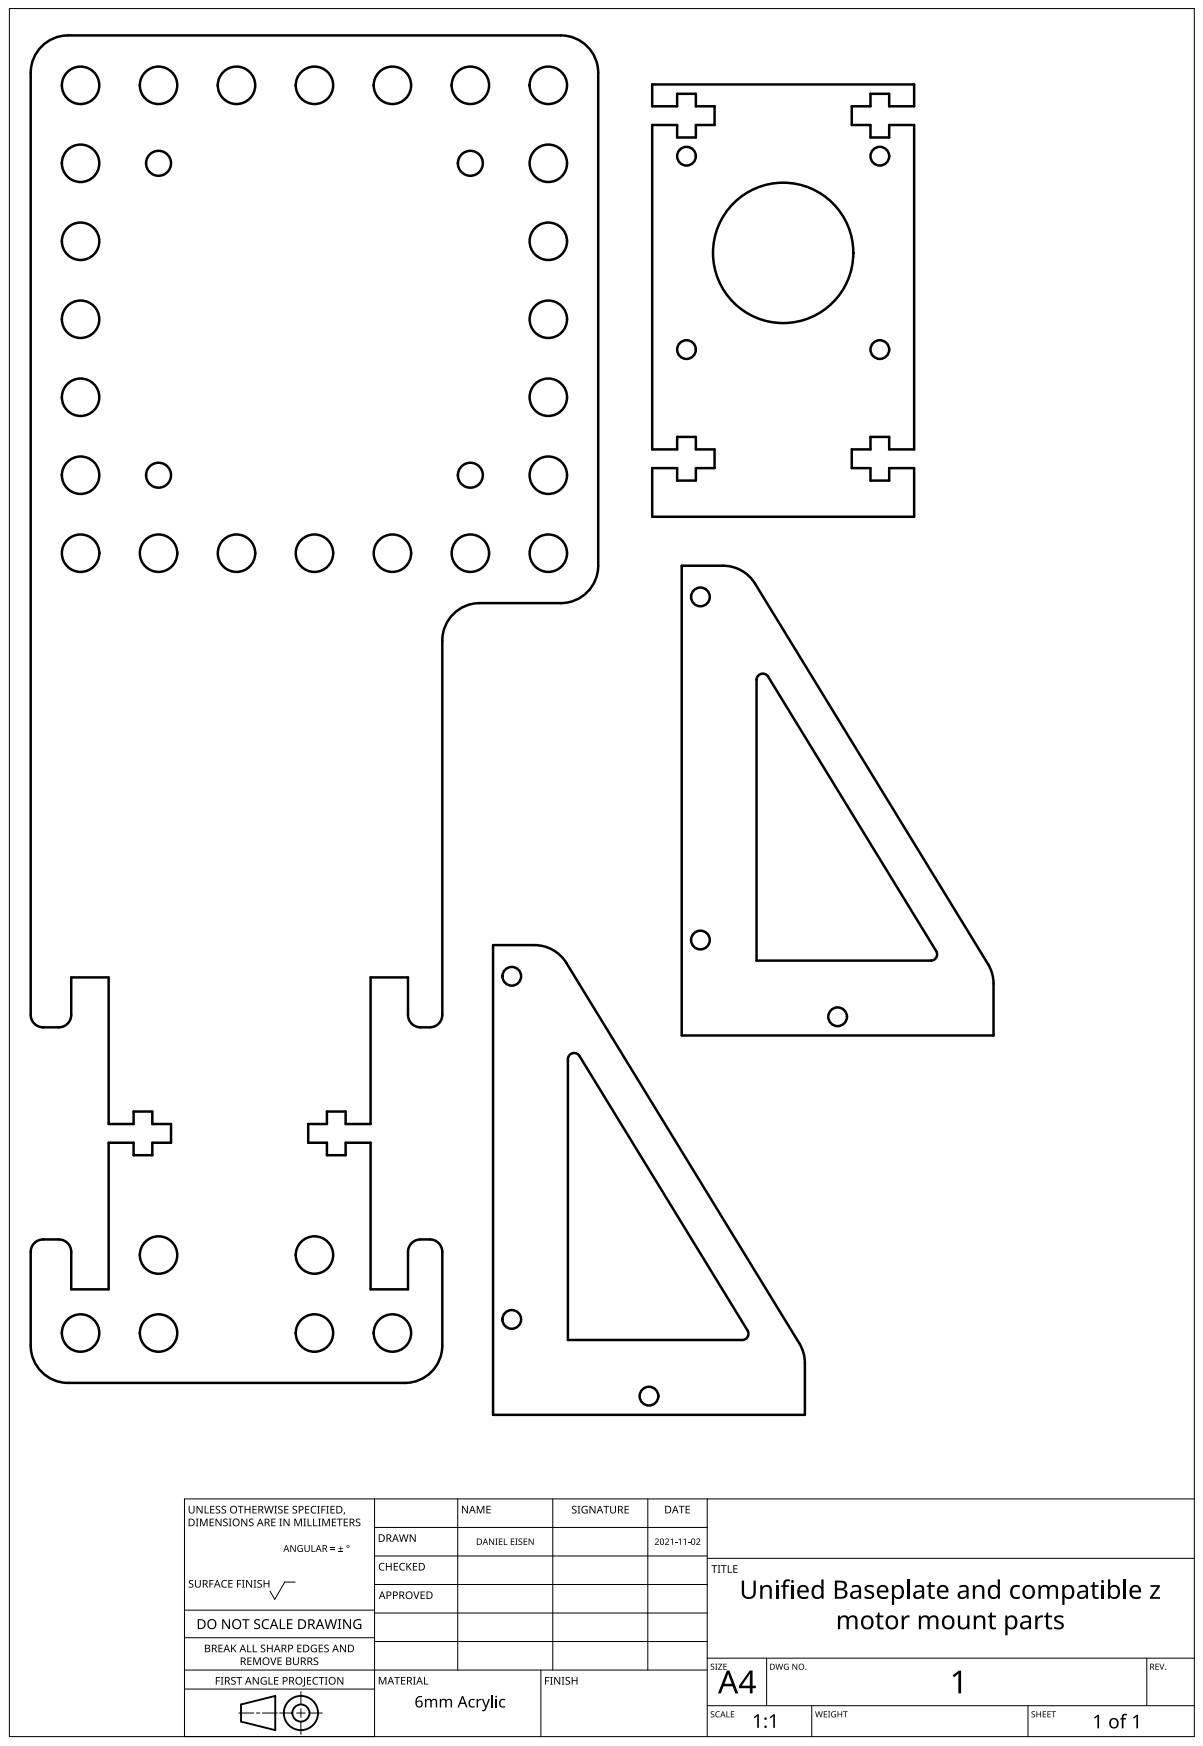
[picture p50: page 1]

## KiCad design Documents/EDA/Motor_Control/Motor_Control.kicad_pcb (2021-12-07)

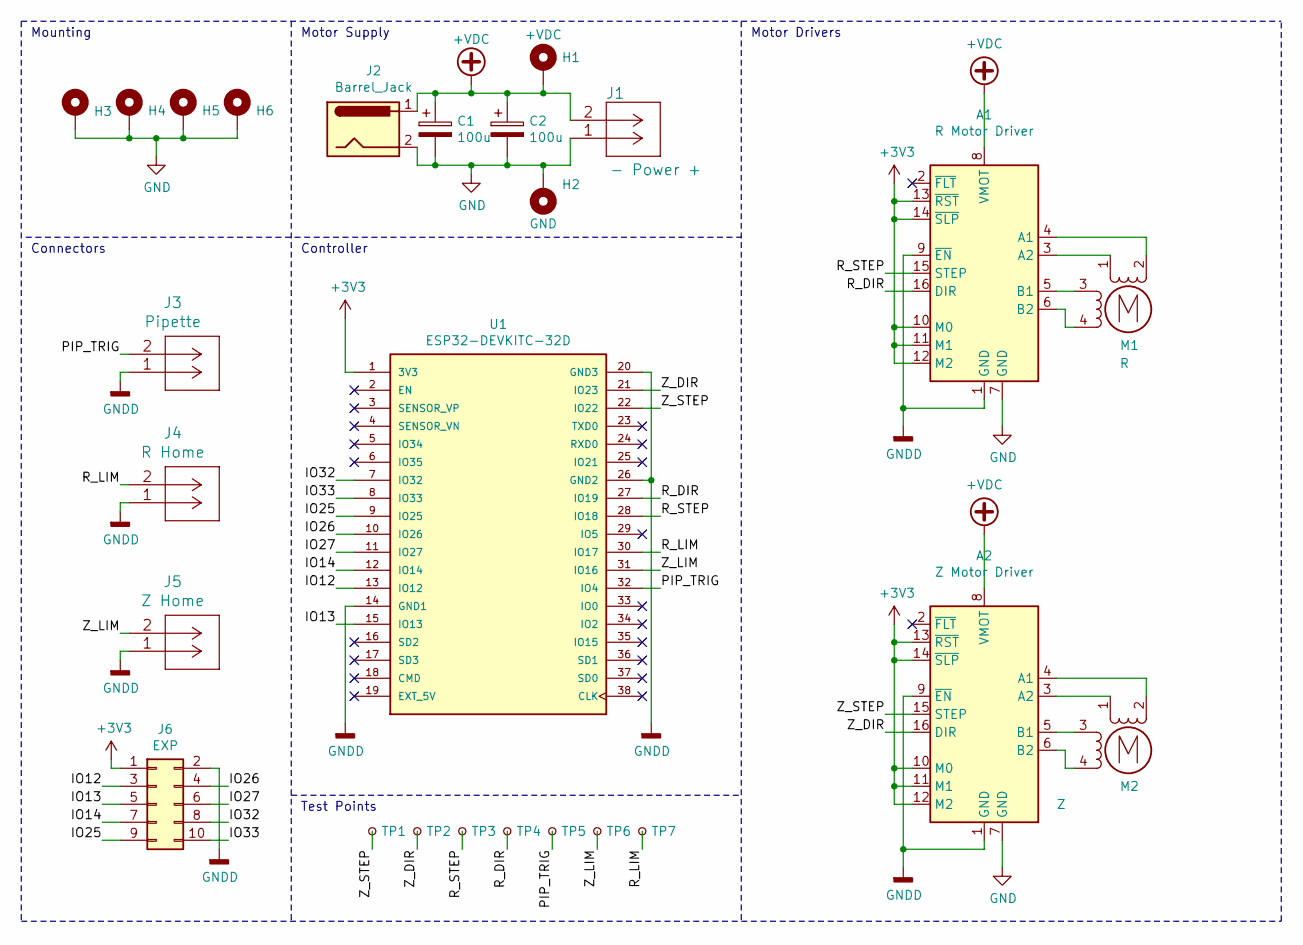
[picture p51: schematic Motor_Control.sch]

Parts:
A1: R Motor Driver; Pololu_Breakout-16_15.2x20.3mm
A2: Z Motor Driver; Pololu_Breakout-16_15.2x20.3mm
C1, C2: 100u; CP_Radial_D8.0mm_P3.50mm
H1: +VDC; MountingHole_3.7mm_Pad_Via
H2: GND; MountingHole_3.7mm_Pad_Via
H3, H4, H5, H6: øM3; MountingHole_3.2mm_M3_Pad_Via
J1: - Power +; molex_sherlock_vrthdr_2pin
J2: Barrel_Jack; BarrelJack_Horizontal; man part # PJ-002BH
J3: Pipette; molex_sherlock_vrthdr_2pin
J4: R Home; molex_sherlock_vrthdr_2pin
J5: Z Home; molex_sherlock_vrthdr_2pin
J6: EXP; PinHeader_2x05_P2.54mm_Vertical
M1: R; molex_sherlock_vrthdr_4pin
M2: Z; molex_sherlock_vrthdr_4pin
TP1: Z_STEP; TestPoint_Pad_D1.0mm
TP2: Z_DIR; TestPoint_Pad_D1.0mm
TP3: R_STEP; TestPoint_Pad_D1.0mm
TP4: R_DIR; TestPoint_Pad_D1.0mm
TP5: PIP_TRIG; TestPoint_Pad_D1.0mm
TP6: Z_LIM; TestPoint_Pad_D1.0mm
TP7: R_LIM; TestPoint_Pad_D1.0mm
U1: ESP32-DEVKITC-32D; MODULE_ESP32-DEVKITC-32D; PARTREV 4

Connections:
+3V3: A1.10 (M0), A1.11 (M1), A1.12 (M2), A1.13 (~RST), A1.14 (~SLP), A2.10 (M0), A2.11 (M1), A2.12 (M2), A2.13 (~RST), A2.14 (~SLP), J6.1, U1.1 (3V3)
+VDC: A1.8 (VMOT), A2.8 (VMOT), C1.1, C2.1, H1.1, J1.2, J2.1
/IO12: J6.3, U1.13 (IO12)
/IO13: J6.5, U1.15 (IO13)
/IO14: J6.7, U1.12 (IO14)
/IO25: J6.9, U1.9 (IO25)
/IO26: J6.4, U1.10 (IO26)
/IO27: J6.6, U1.11 (IO27)
/IO32: J6.8, U1.7 (IO32)
/IO33: J6.10, U1.8 (IO33)
/PIP_TRIG: J3.2, TP5.1, U1.32 (IO4)
/R_DIR: A1.16 (DIR), TP4.1, U1.27 (IO19)
/R_LIM: J4.2, TP7.1, U1.30 (IO17)
/R_STEP: A1.15 (STEP), TP3.1, U1.28 (IO18)
/Z_DIR: A2.16 (DIR), TP2.1, U1.21 (IO23)
/Z_LIM: J5.2, TP6.1, U1.31 (IO16)
/Z_STEP: A2.15 (STEP), TP1.1, U1.22 (IO22)
GND: A1.7 (GND), A2.7 (GND), C1.2, C2.2, H2.1, H3.1, H4.1, H5.1, H6.1, J1.1, J2.2
GNDD: A1.1 (GND), A1.9 (~EN), A2.1 (GND), A2.9 (~EN), J3.1, J4.1, J5.1, J6.2, U1.14 (GND1), U1.20 (GND3), U1.26 (GND2)
unnamed: A1.3 (A2), M1.1
unnamed: A1.4 (A1), M1.2 (-)
unnamed: A1.5 (B1), M1.3
unnamed: A1.6 (B2), M1.4
unnamed: A2.3 (A2), M2.1
unnamed: A2.4 (A1), M2.2 (-)
unnamed: A2.5 (B1), M2.3
unnamed: A2.6 (B2), M2.4

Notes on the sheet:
Motor Supply
Motor Drivers
Controller
Connectors
Mounting
Test Points

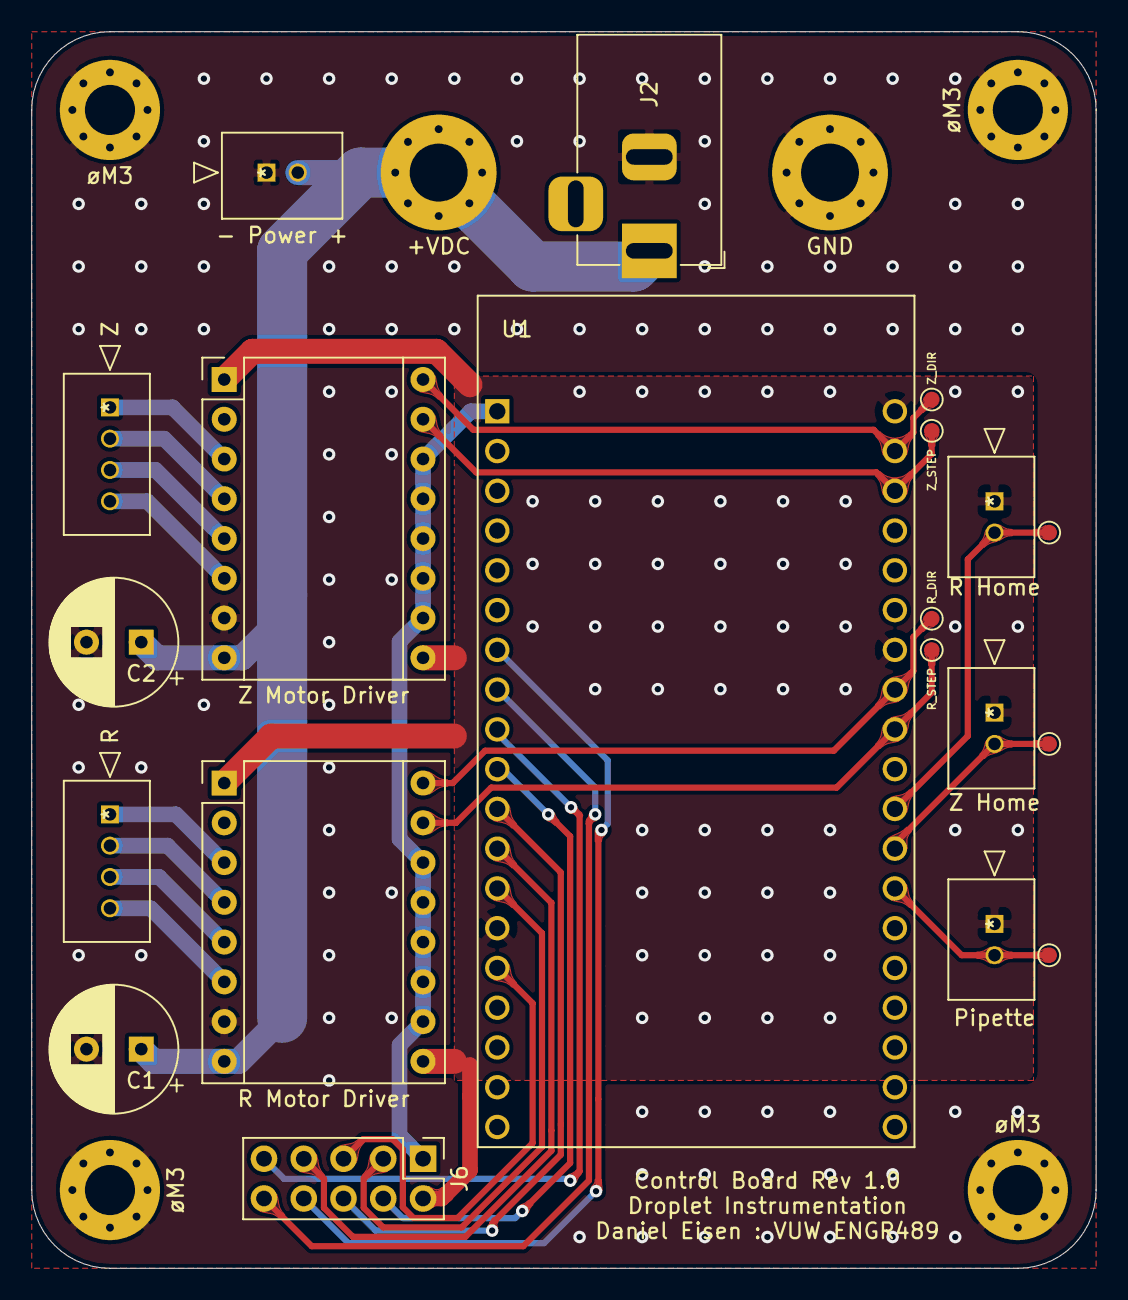
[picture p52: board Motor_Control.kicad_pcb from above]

Board: 2 copper layers, 68.0 x 79.0 mm, 26 parts (0 on the bottom side), 27 nets.

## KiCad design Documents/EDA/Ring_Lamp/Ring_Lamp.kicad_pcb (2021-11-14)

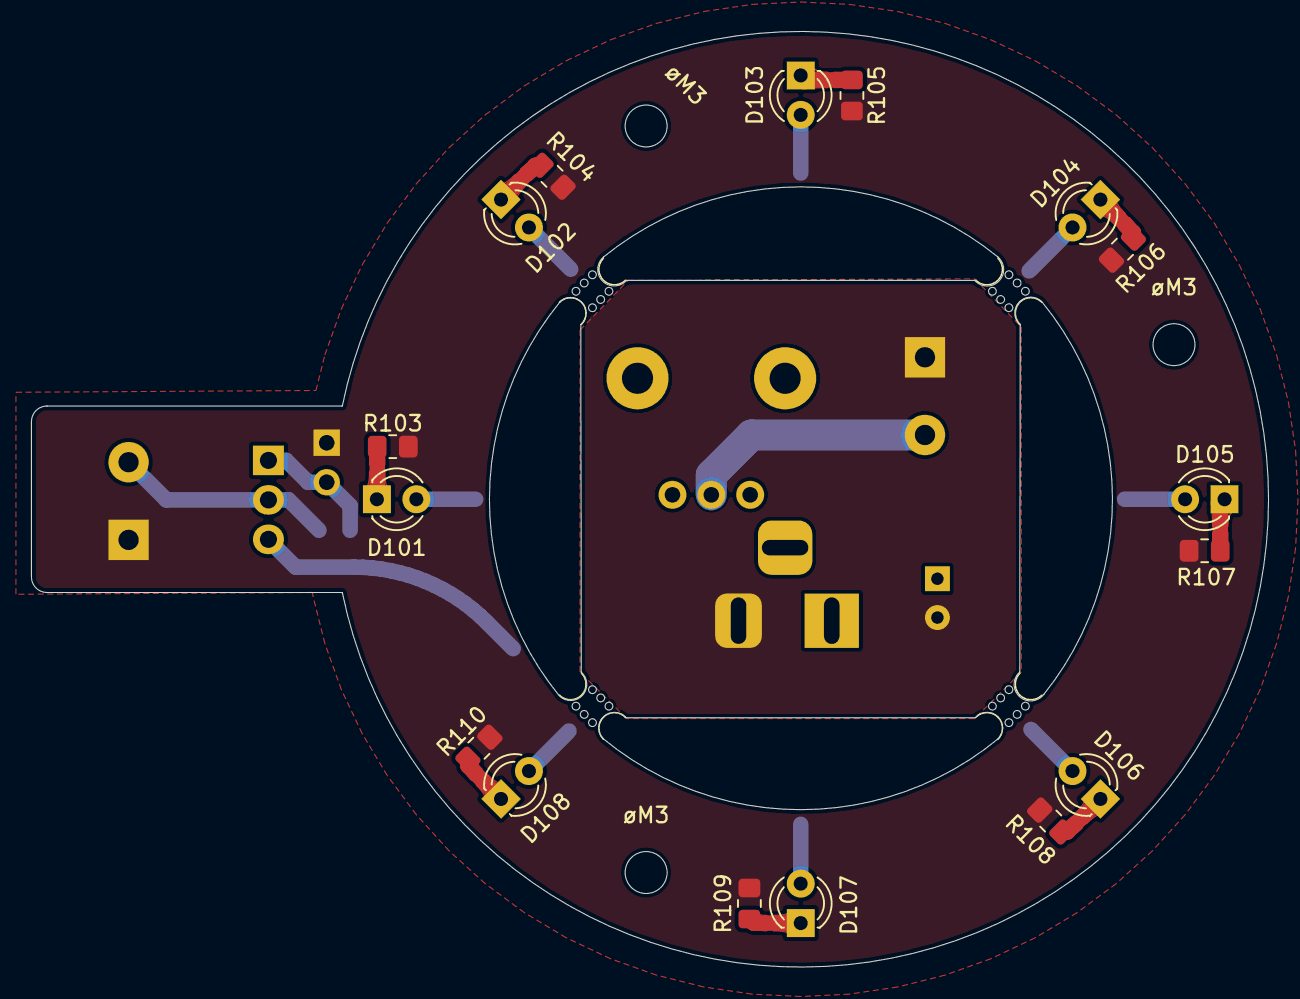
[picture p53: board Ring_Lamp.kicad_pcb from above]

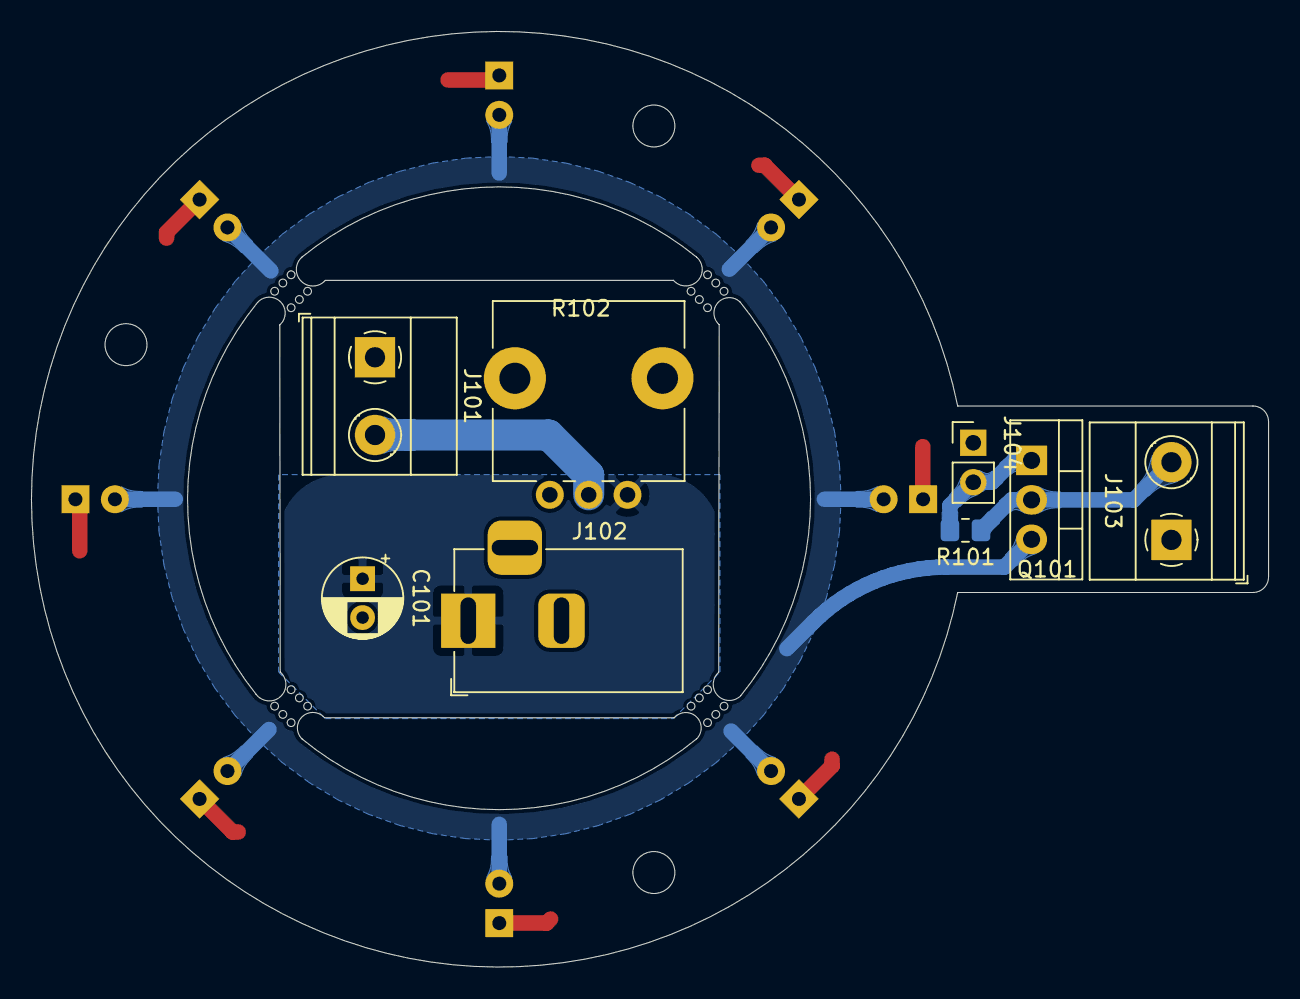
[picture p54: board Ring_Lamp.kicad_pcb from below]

Board: 2 copper layers, 79.6 x 60.2 mm, 31 parts (8 on the bottom side), 13 nets.

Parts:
C101: 100u; CP_Radial_D5.0mm_P2.50mm
D101, D102, D103, D104, D105, D106, D107, D108: LED; LED_D3.0mm_Clear
J101: CTRL_V_LED; TerminalBlock_Phoenix_MKDS-1,5-2_1x02_P5.00mm_Horizontal
J102: Barrel_Jack; BarrelJack_Horizontal
J103: RING_V_LED; TerminalBlock_Phoenix_MKDS-1,5-2_1x02_P5.00mm_Horizontal
J104: ENABLE; PinHeader_1x02_P2.54mm_Vertical
Q101: Q_NMOS_GDS; TO-220-3_Vertical
R101: 10k; R_0805_2012Metric_Pad1.20x1.40mm_HandSolder
R102: 10k; Potentiometer_Alps_RK09L_Single_Vertical
R103, R104, R105, R106, R107, R108, R109, R110: 100; R_0805_2012Metric_Pad1.20x1.40mm_HandSolder
mouse-bite-2mm-slot, mouse-bite-2mm-slot#2, mouse-bite-2mm-slot#3, mouse-bite-2mm-slot#4: VAL**; mouse-bite-2mm-slot
øM3, øM3#2, øM3#3: MountingHole; MountingHole_2.7mm_M2.5

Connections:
/ENABLE: J104.2, Q101.1, R101.2
/LED_BUS: D101.2, D102.2, D103.2, D104.2, D105.2, D106.2, D107.2, D108.2, Q101.3
/V_LED: J101.2, J103.2, Q101.2, R101.1, R102.2
GND: C101.2, J101.1, J102.2, J103.1, J104.1, R103.1, R104.1, R105.1, R106.1, R107.1, R108.1, R109.1, R110.1
unnamed: D101.1, R103.2
unnamed: D102.1, R104.2
unnamed: D103.1, R105.2
unnamed: D104.1, R106.2
unnamed: D105.1, R107.2
unnamed: D106.1, R108.2
unnamed: D107.1, R109.2
unnamed: D108.1, R110.2
VDD: C101.1, J102.1, R102.1

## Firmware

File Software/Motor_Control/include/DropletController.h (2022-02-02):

#ifndef DROP_CONTROLLER
#define DROP_CONTROLLER

#include <ESP_FlexyStepper.h>
#include "CameraTrigger.h"

const uint8_t INPUT_SIZE = 64;

// IO pin assignments
const uint8_t R_MOTOR_STEP_PIN = 18;
const uint8_t R_MOTOR_DIRECTION_PIN = 19;
const uint8_t R_HOME = 17;

const uint8_t Z_MOTOR_STEP_PIN = 22;
const uint8_t Z_MOTOR_DIRECTION_PIN = 23;
const uint8_t Z_HOME = 16;

const uint8_t DROP_TRIG = 4;

//motor config
const uint8_t STEP_DIV = 32;
const uint32_t REV_STEPS = 200 * STEP_DIV;


void go_home(); 
void init_steppers();
void execute_command(char *input);
void command_loop();

#endif //DROP_CONTROLLER

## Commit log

2021-03-30 motor research
2021-05-05 Updated mount and stage spec
2021-05-19 prelim andatasheets
    [eisendani_489-BOM order.xlsx, eisendani_489-BOM.xlsx]
2021-05-19 parts and cad
    [Part Studio 1 - mount_adapt.stl, Part Studio 1 - ring_clamp.stl, Part Studio 1 - ring_clamp_5mm.stl, Part Studio 1 - ring_clamp_wide.stl]
2021-06-04 motor addition to cad/eda and datasheets
    [Motor_Control.kicad_pcb, Motor_Control.sch]
2021-06-15 FIN v0.1 of serial control
    [ring_clamp_a_32.stl, ring_clamp_b_36.stl, ring_clamp_b_38.stl]
2021-06-15 hotfix: Serial printing
2021-06-17 z micrometer coupler stl
    [Z_umeter_coupler - slide_coupler.stl]
2021-06-28 z mount fin rev 1
2021-07-19 PCB first pass
    [Motor_Control.sch]
2021-08-16 rev 2 parts
    [Z_umeter_coupler - slide_coupler_rev2.stl, ring_clamp_a_32_rev2.stl, ring_clamp_b_36_rev2.stl]
2021-08-17 libs and pcb and bom
    [Motor_Control.kicad_pcb, Motor_Control.sch]
2021-08-17 connectors placed
    [Motor_Control.kicad_pcb, Motor_Control.sch]
2021-08-26 Final pcb and bom
    [Motor_Control.kicad_pcb, Motor_Control.sch, eisendani_489-BOM order II.xlsx]
2021-09-16 PCB complete and ordered
    [Motor_Control-B_Cu.gbr, Motor_Control-B_Mask.gbr, Motor_Control-B_Paste.gbr, Motor_Control-B_SilkS.gbr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]
2021-09-21 labview control
    [backup.xlsx, test.xlsx]
2021-09-22 temp aq
    [R1.xlsx, backup.xlsx, test.xlsx]
2021-09-26 calibration images 22_9
2021-09-28 reimplented deep sleep to fix pin alarm and sleep periferals
2021-11-04 Ring light for camera illum
    [Ring_Lamp.kicad_pcb, Ring_Lamp.sch]
2021-11-14 ring light
    [Motor_Control.kicad_pcb, Motor_Control.sch, Ring_Lamp.kicad_pcb, Ring_Lamp.sch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]
2021-11-22 homing fully intergrated
    [SS_3GLP.step]
2021-12-03 color coding
    [eisendani_drop_instr_RA-BOM_order.xlsx]
2021-12-13 GUI camera config and control
2021-12-15 camera triggering

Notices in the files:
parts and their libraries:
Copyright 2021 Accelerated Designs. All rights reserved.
